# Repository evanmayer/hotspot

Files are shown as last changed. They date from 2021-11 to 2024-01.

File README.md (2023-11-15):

This repo contains code that is a part of the [TIME collaboration](https://ui.adsabs.harvard.edu/abs/2014SPIE.9153E..1WC/abstract).

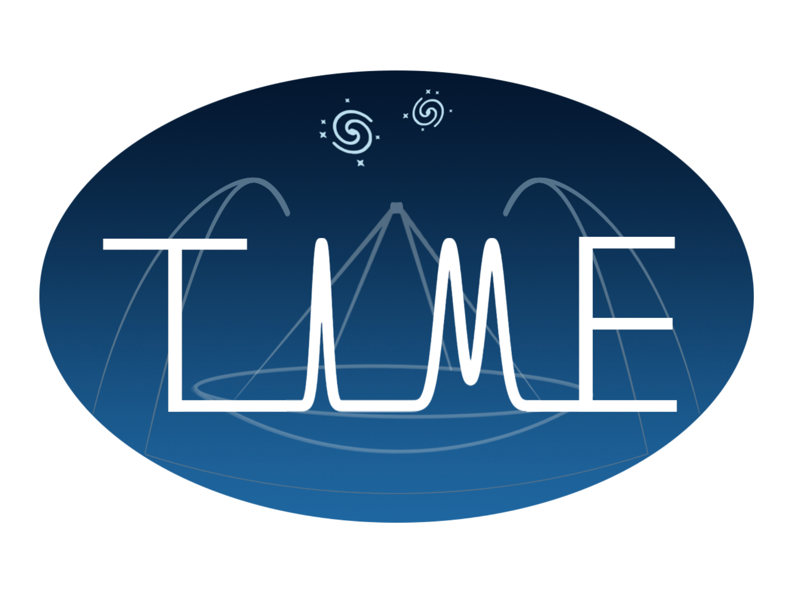
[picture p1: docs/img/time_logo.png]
TIME Collaboration


Logo by Guochao (Jason) Sun.

# hotspot

Code for driving a cable-driven parallel robot for mapping beams on surfaces.

The robot moves and controls switchable thermal infrared sources to scan a 2D x-y plane, and is capable of absolute accuracy at the <3 mm level over a workspace ~0.40m x 0.40m.

## Running

Run `python main.py -h` for the docstring describing the command line interface.

### Example

```bash
python main.py ./data/input/geometry/frame.csv ./data/input/profiles/circle.csv
```

## Other Documentation

See the [HOWTO](HOWTO.md).

## Contributing

### Testing
Testing is accomplished with `pytest`. Passing tests are a prerequisite for committing code, and new code should come with new tests.

To run the test suite defined in the `tests` dir, change dir to the toplevel dir of the repo and execute 
```bash
pytest
```

### Pushing changes
If you need push permissions, message me. Otherwise, you may fork, create a new branch with your changes, and fill out a Pull Request to have the changes reviewed and merged in.

### How did you make your algorithm flowcharts?
[diagrams.net](https://diagrams.net)

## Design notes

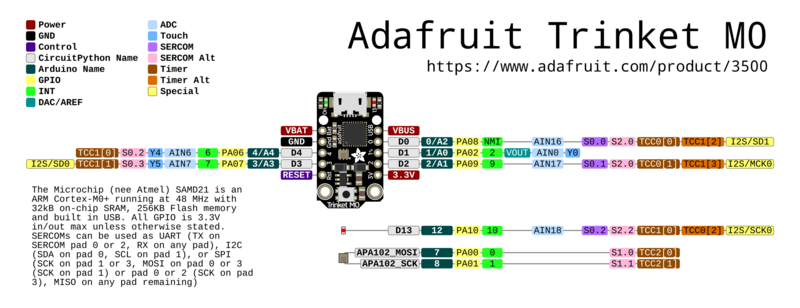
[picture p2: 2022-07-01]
docs/html/docs/img/adafruit_products_Adafruit_Trinket_M0_pinout.png

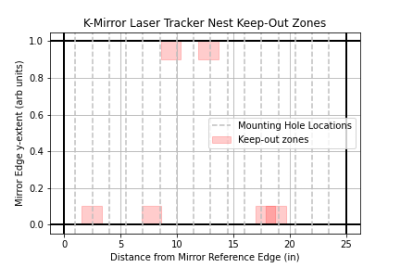
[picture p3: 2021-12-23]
docs/html/docs/img/keepout.png

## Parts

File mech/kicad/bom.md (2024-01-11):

# Bill of Materials

2024-01-11 Evan C. Mayer

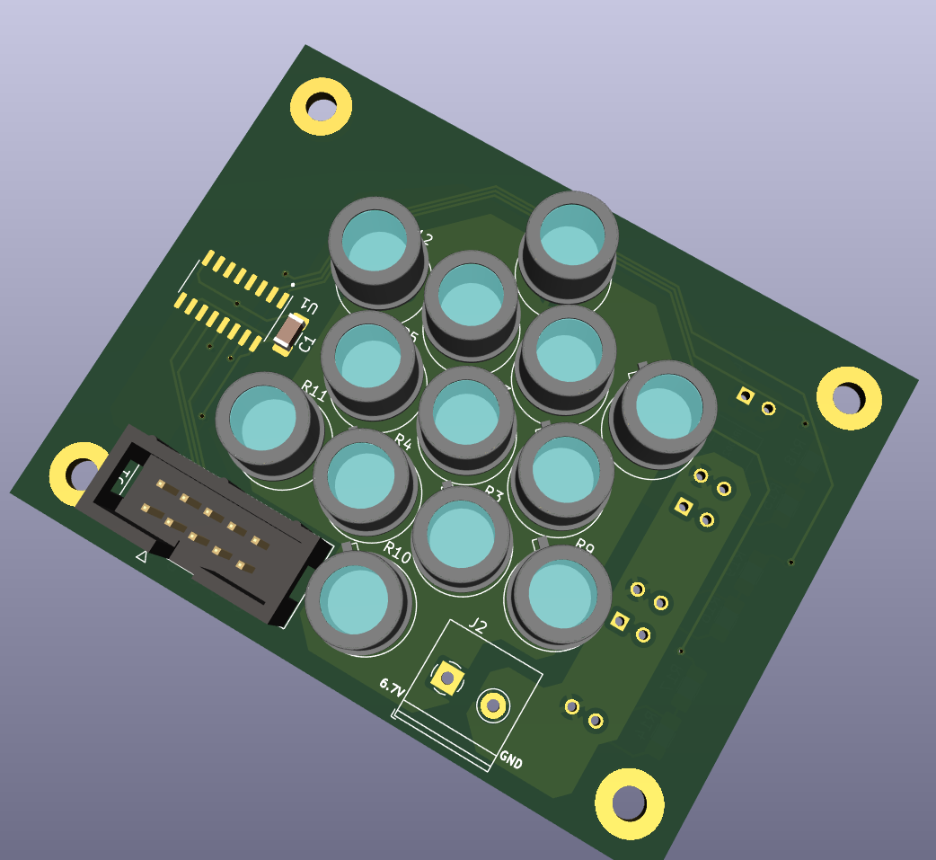
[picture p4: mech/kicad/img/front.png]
Front


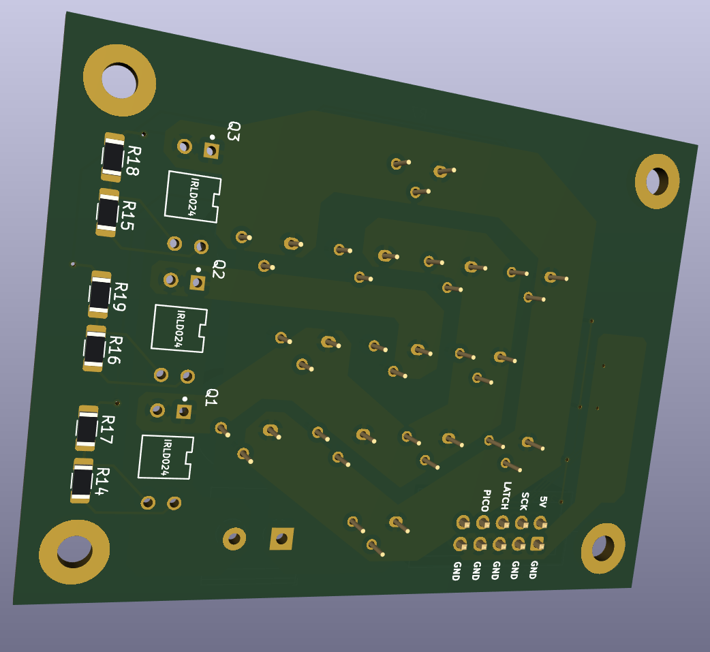
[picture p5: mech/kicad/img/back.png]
Back


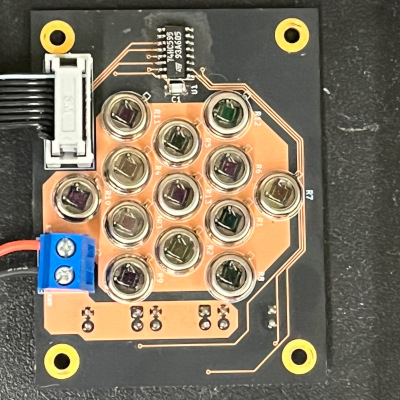
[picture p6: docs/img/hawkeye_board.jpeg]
Built


## Components

Originally developed to be driven by a microcontroller, with each ring selectable via a shift register circuit. If you send a logic-level square wave to MOSFETs some other way, you may omit the items necessary for the shift register driver circuit, marked with an asterisk.

| Part Name | Vendor | Part No. | Link | Qty. | Approx. Cost (USD ea.) | Rationale |
| -- | -- | -- | -- | -- | -- | -- |
Modulated Infrared Source | Hawkeye Technologies | IR-50 | [Link](http://www.hawkeyetechnologies.com/source-selection/pulsable/#ir5x/) [Alt.](https://shop.boselec.com/products/ir-50-ir-55) | 13 | 70.00 | Infrared Emitter |
| Carrier Board | Oshpark | - | [Link](https://oshpark.com/shared_projects/rne2hvI5) | 3 | 10.03 | Assembly/Signal/Power delivery |
| Power MOSFET | Digikey | IRLD024 (sub. IRLD024PBF) | [Original](https://www.digikey.com/en/products/detail/vishay-siliconix/IRLD024/51139) [Sub.](https://www.digikey.com/en/products/detail/vishay-siliconix/IRLD024PBF/812492) | 3 | 1.88 | Power switching via logic-level inputs |
| Resistor 1 | Digikey | RMCF1206JT100R | [Link](https://www.digikey.com/en/products/detail/stackpole-electronics-inc/RMCF1206JT100R/1757426) | 3 | 0.10 | Voltage divider upper. Any 100 Ohm 1/4 W SMD 1206 package. |
| Resistor 2 | Digikey | RMCF1206FT10K0CT-ND | [Link](https://www.digikey.com/en/products/detail/stackpole-electronics-inc/RMCF1206FT10K0/1759669) | 3 | 0.10 | Voltage divider lower. Any 10 kOhm 1/4 W SMD 1206 package. |
| Terminal block | Tri-tek | PHITB132 (sub. TO0201520000G-ND) | [Original](https://www.tritekelectronics.com/wire-termination/terminal-blocks-and-barrier-strips/philmore-tb132) [Sub.](https://www.digikey.com/en/products/detail/amphenol-anytek/TO0201520000G/4953320) | 1 | 0.50 | Power wire connection |
| Shift Register* | Digikey | NTE74HC595T | [Link](https://www.digikey.com/en/products/detail/nte-electronics-inc/NTE74HC595T/11650421?s=N4IgTCBcDaIHYBcCmB2ALACQMIFYCcOIAugL5A) | 1 | 0.55 | Addressable outputs for power switching |
| I2C capacitor* | Digikey | 2368-SMC1206Z104-ND | [Link](https://www.digikey.com/en/products/detail/nte-electronics-inc/SMC1206Z104/11644126) | 1 | 0.05 | I2C noise decoupling capacitor |
| Ribbon cable termination* | Digikey | MSC10A-ND | [Link](https://www.digikey.com/en/products/detail/3m/89110-0001/229679) | 1 | 1.45 | Mates to pins on board header |
| I2C header* | Digikey | 30310-6002HB-ND | [Link](https://www.digikey.com/en/products/detail/3m/30310-6002HB/1237393) | 1 | 0.75 | Provides pwr, I2C header to shift register on board |
| I2C cable* | Adafruit | 3890 | [Link](https://www.adafruit.com/product/3890) | 1 | 3.95 | Sub. any 5-10 conductor 28 AWG ribbon cable if flexible silicone insulation not needed.
| Adafruit Trinket M0 Microcontroller* | Adafruit | 3500 | [Link](https://www.adafruit.com/product/3500) | 1 | 8.95 | Sends bytes to shift register over I2C to chop IR source banks on/off. Sub. any Arduino-compatible microcontroller, with slight code changes.

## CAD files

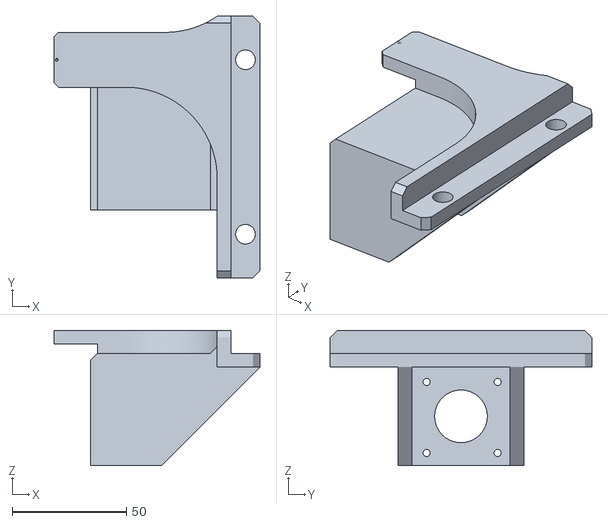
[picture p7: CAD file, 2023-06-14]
mech/3d_prints/motor_mount_thin_mirror.stl
90.0 x 114.3 x 59.0

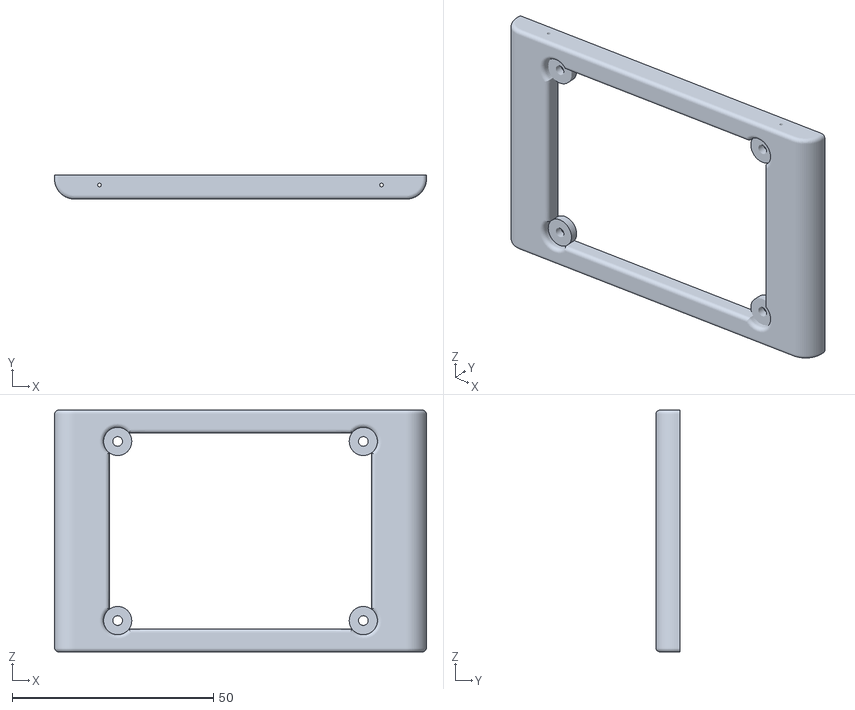
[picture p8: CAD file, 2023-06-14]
mech/3d_prints/hawkeye_raft.stl
92.3 x 6.00 x 60.0

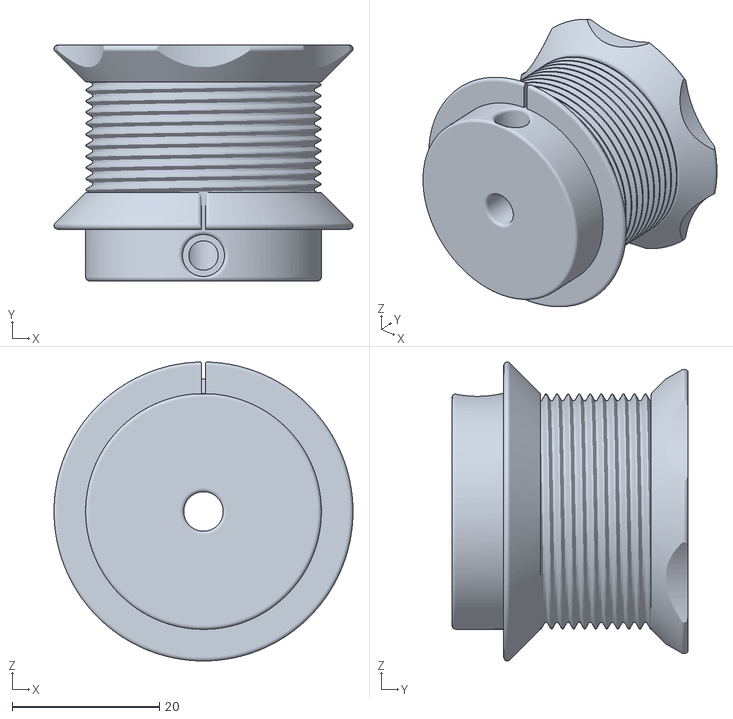
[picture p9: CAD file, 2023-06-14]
mech/3d_prints/drum.stl
40.6 x 32.0 x 40.6

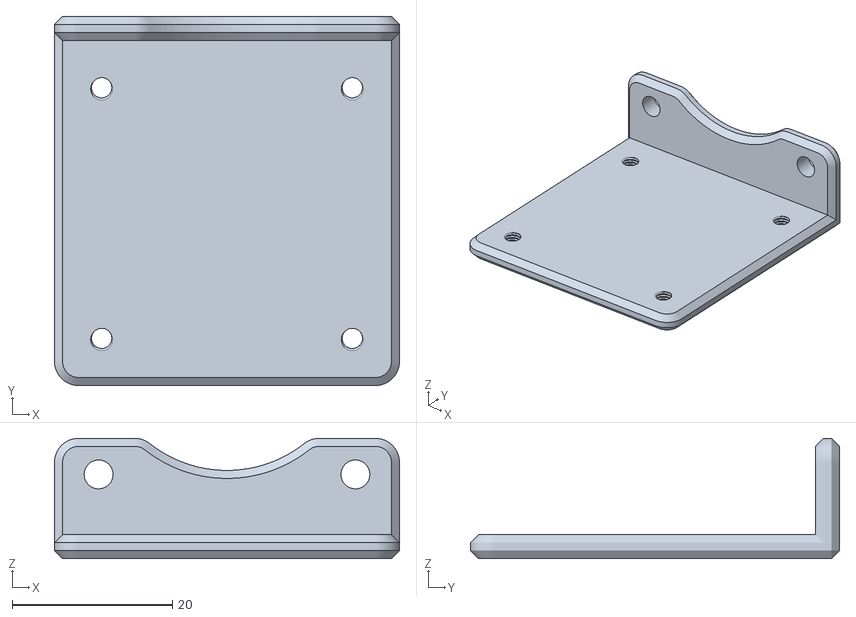
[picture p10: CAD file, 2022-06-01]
mech/3d_prints/ezstepper_bracket.stl
43.0 x 46.0 x 15.0

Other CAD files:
mech/3d_prints/motor_mount_thin.stl

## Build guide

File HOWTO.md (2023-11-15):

# How To

This doc contains instructions for various tasks related to setting up and running the `hotspot` mirror mapper.

#### What is `hotspot`?

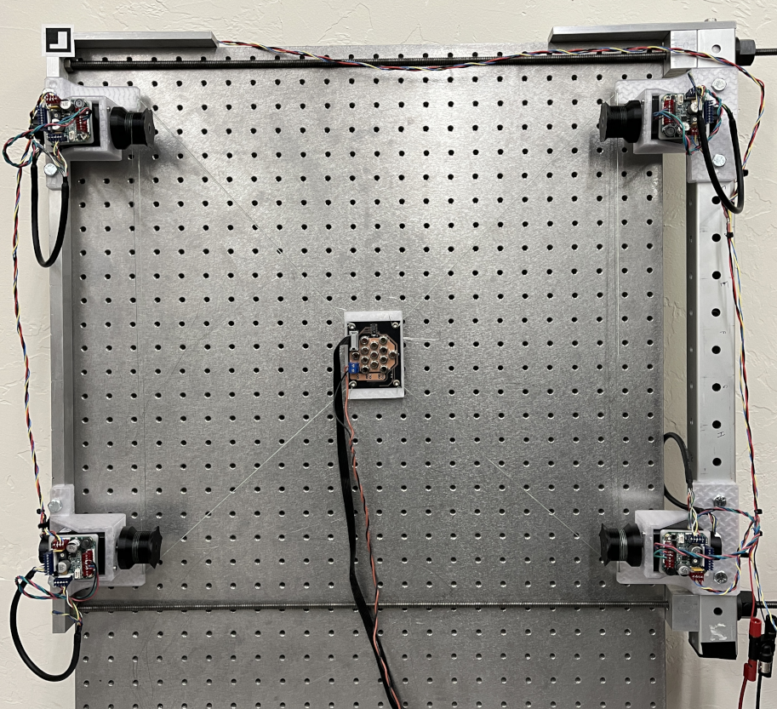
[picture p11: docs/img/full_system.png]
entire system


`hotspot` is a planar cable-driven parallel robot (CDPR), with four stepper motors that move a central raft of hot IR sources by changing the length of cables attached to it. The cables are fixed to an adjustable frame. The frame can clamp to any rectangular surface, but it was designed to clamp to various relay mirrors that couple radiation from the sky to the TIME spectrometer inside the receiver cabin on the ARO 12 meter telescope on Kitt Peak, allowing an electronically controlled, hot, IR-emitting source to be swept across the mirror to observe the detectors' spatial response.

#### What is this document?

This document is a comprehensive how-to on setting up, maintaining, and running the mirror mapper. It contains all the information that would be needed to replace and reconfigure major components of the system, however unlikely that may be.

It is organized in order of information flow: from the operator (you!) logging into the control computer, to setting up the software environment, connecting the power and signal cables, assembling the mapper frame, creating input files, mounting it on various mirrors, and operating the mapper. 

## Using the control computer

The mapper motors are controlled by running the `main.py` application on a computer with a [USB-to-RS485 adapter](https://www.uotek.com/pro_view-122.html). The IR sources are controlled via a USB cable connected to a microcontroller. You should check out the `hotspot` repo if you wish to run the mapper or [generate new input files](#ok-but-is-there-an-easy-way-to-make-a-new-one).

## Setting Up the Environment

To run `hotspot`, you must satisfy the dependencies. They are enumerated in `environment.yml`, a human-readable file that can be ingested by the `conda` Python package manager.

#### Is the environment set up?

First, check that the environment setup has not been done before. If 

```bash
conda activate hotspot
```
succeeds, skip to [software testing with pytest](#software-testing-with-pytest).

### Anaconda

#### Is Anaconda set up?

If the Python environment/package manager [Anaconda](https://www.anaconda.com/) does not exist on the computer you're running this on, I recommend installing Miniconda according to [the instructions](https://docs.conda.io/en/latest/miniconda.html#installing).

Once that is done, we are ready to set up the `hotspot` environment. `conda` environments keep a project's dependencies from polluting your computer's environment and make sure they all play nicely together. `conda` allows specifying the dependencies needed in a file with a `.yml` extension. This is done for you. Create the `hotspot` conda env with

```bash
conda env create -f environment.yml
```

It should install things like `numpy` and `matplotlib`, as well as libraries for the hardware, such as the `pyserial` library for driving the steppers. There are also packages for documentation.

> **NOTE:** packages needed for post-processing of photos to measure mapper performance or for producing predicted beam maps using the code in the `verification/` folder are not covered by this `.yml`. Aside from OpenCV they are just standard scientific Python packages, so the requirements should be easy to meet if this code is needed.

### Keeping things up to date

If you need to install something new later on with `conda install` or `pip`, remember to update `environment.yml` by doing 

```bash
conda env export --from-history | tee environment.yml
```

If your `environment.yml` has been updated, and you need to update your env with the new `environment.yml`, do

```bash
conda env update --file environment.yml --prune
```

## Software Testing with `pytest`

In order to verify that basic low-level functionality is unbroken, run `pytest` from the toplevel directory of the repo.

## Power

### Motors

#### Do the motor driver boards have power?

Each motor is controlled by an [AllMotion EZStepper EZHR17EN](https://www.americancontrolelectronics.com/ezhr17en). These are [chopper driver](https://homepage.divms.uiowa.edu/~jones/step/current.html#pwm) boards that accept 10-40 V input.

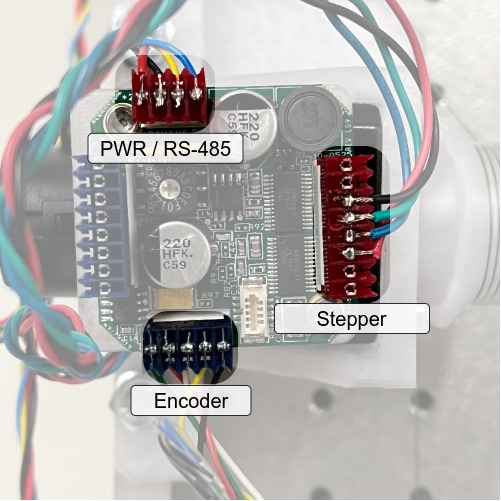
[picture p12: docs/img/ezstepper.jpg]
photo of EZStepper board


Configure a constant-voltage DC power supply to provide:

* 24 V
* 4 A

The EZStepper drivers are configured in software to draw 50% of the rated 2 A current = 1 A each, for a total of 4 A. In use, the motors may draw somewhat less current.

> **Note:** See the AllMotion/American Control Electronics wiring diagram to identify the Vin and GND inputs.

### Hawkeyes

#### Do the Hawkeyes have power?

The Hawkeyes are mounted on a PCB and powered by a power supply connected to the screw terminal. Positive and ground terminals are labeled on the PCB silkscreen (white text).

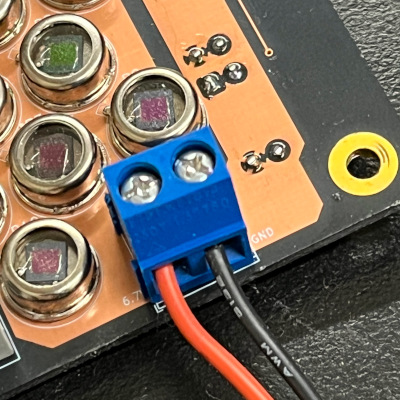
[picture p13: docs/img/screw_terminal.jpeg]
photo of screw terminal


Requirements:

* 6.7 V (constant voltage)
* ≥ 2 A

The Hawkeye IR-50 source temperature depends on the voltage applied, and the current draw depends on the voltage (see datasheet in `pdf` dir). The design target temperature is 750 C, requiring a voltage of 6.7V and a current of ~134mA per source, for a total current draw of ~1.74A when all sources are turned on. In practice, Hawkeye sources have not drawn quite this much current.

There will be some voltage drop at the screw terminal; this is normal. If one source is powered, the voltage drop is negligible, but if all 13 sources are powered, the voltage drop is approximately .22 V. Do not attempt to compensate for this at the power supply! If you turn up the supply voltage to 6.9 V to get 6.7 V under a 13 source load, a load of a single source will see 6.9 V, drastically reducing its lifetime.

### Hawkeye Microcontroller

The Hawkeye sources are turned on and off by an Adafruit Trinket M0 microcontroller. It gets 5V power via a micro USB cable.

#### Does the microcontroller have power?

The Trinket M0's power LED will illuminate when it is connected to the USB port. The Trinket GND pin should be connected to the Hawkeye power supply's ground terminal.

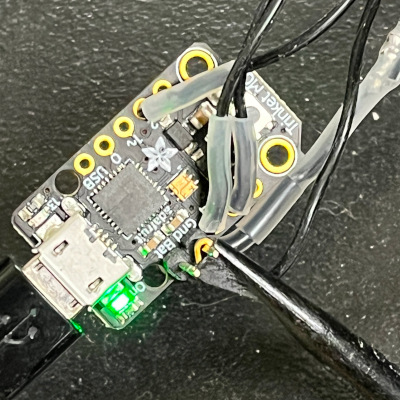
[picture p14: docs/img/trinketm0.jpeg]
photo of mcu on


## Frame

#### Is the frame fully assembled?

The 3D printed stepper motor mounts are attached to the beam mapper frame by 5/16-18 x 2" or 2.25" bolts with nyloc "jam" nuts.

Two aluminum registration tabs are screwed into the end of each frame piece opposite the black plastic end caps, using a 5/16-18 x 1/4" screw. They are long enough to reach an edge of the mirror regardless of if the mirror's corners have been machined off. 

> **NOTE:** These tabs register the frame to a third edge of the mirror, so **it is important that they not be bent**.

Long 5/16-18 steel threaded rods connect the two halves of the frame. On one end of the threaded rods, threads in the aluminum extrusion provide clamping force. On the other end of the threaded rod, a slide-adjust nut with a thumb button allows easily changing the distance between clamping surfaces, and applies clamping force to the outside of the opposite aluminum extrusion. Care should be exercised with this slide-adjust nut, as pressing the button will release any tension on the threaded rod.

## Serial Communications

We will be talking to devices over serial. 

### Windows

Windows users may need to open `hotspot/constants.py` and edit the `COM` values to match the COM ports assigned to the Hawkeye microcontroller and USB-to-RS485 converter by the OS.

### Ubuntu

On Ubuntu, our user must be a part of a special group to talk to devices over serial. To see the groups your user is a part of, type `groups` in a command prompt.

Add yourself to the `tty` and `dialout` groups, then log out and back in to have the changes take effect:

`sudo usermod -a -G tty $USER`

`sudo usermod -a -G dialout $USER`

## Motion Outputs

### Motors

#### Can the computer talk to the motor drivers?

The EZHR17EN stepper drivers receive commands from a control computer running the `hotspot` software as bytes over the [RS485](https://hackaday.com/2022/04/05/hacker-dictionary-rs-485-will-go-the-distance/#more-528633) physical layer.

> **Note:** Refer to the AllMotion/American Control Electronics EZHR17EN wiring diagram to verify that the RS485 communications connection is correct.

The control computer needs either a 9-pin serial output port, or a USB-to-RS485 adapter to send bytes out over the RS485 bus. The inverting/non-inverting outputs are blue and yellow wires. If you are connecting your adapter to the bus for the first time, you may have to [guess incorrectly](https://en.wikipedia.org/wiki/RS-485#Signals) and swap the wires before it will work.

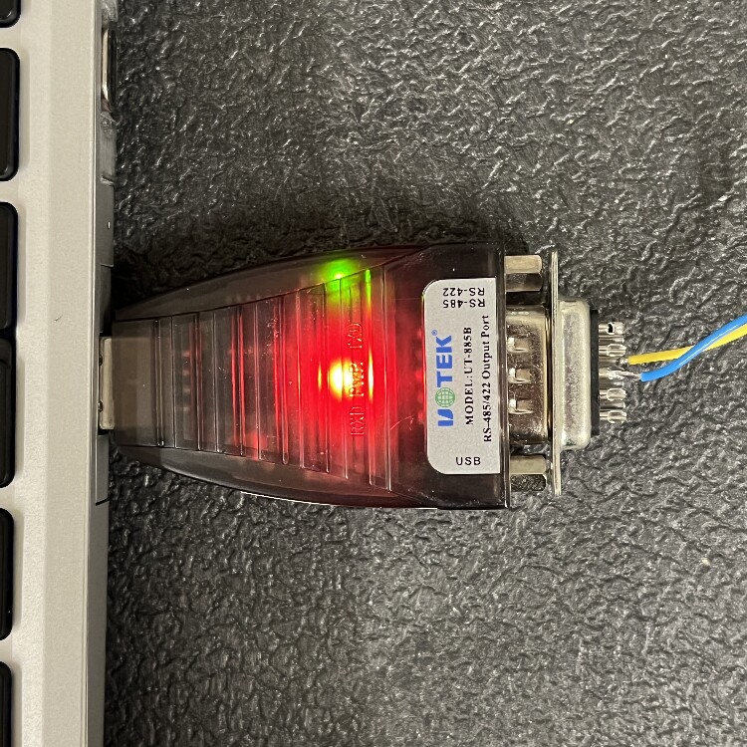
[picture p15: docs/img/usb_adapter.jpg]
photo of USB-RS485 adapter


The motor drivers must have power and ground (via the 24 VDC power supply) to receive commands.

> **NOTE:** RS-485 Connections ought to have a ground wire, although you don't see one pictured here. This is to ensure the differential signal at each receiver is biased correctly. If you experience communication issues on the RS-485 bus, ensure proper grounding.

#### Can the motor drivers command the motors?

> **Note:** Refer to the AllMotion/American Control Electronics EZHR17EN wiring diagram to verify that the motor winding connections are correct.

The stepper motors themselves have NEMA-17 spec hole patterns, which mate to the 3D printed motor mount brackets which are attached to the beam mapper frame. Each stepper motor should be attached to its motor mount using M3 x 0.5 x 10 mm screws. If attaching motors for the first time, use lubricant, because metal on plastic will be squeaky.

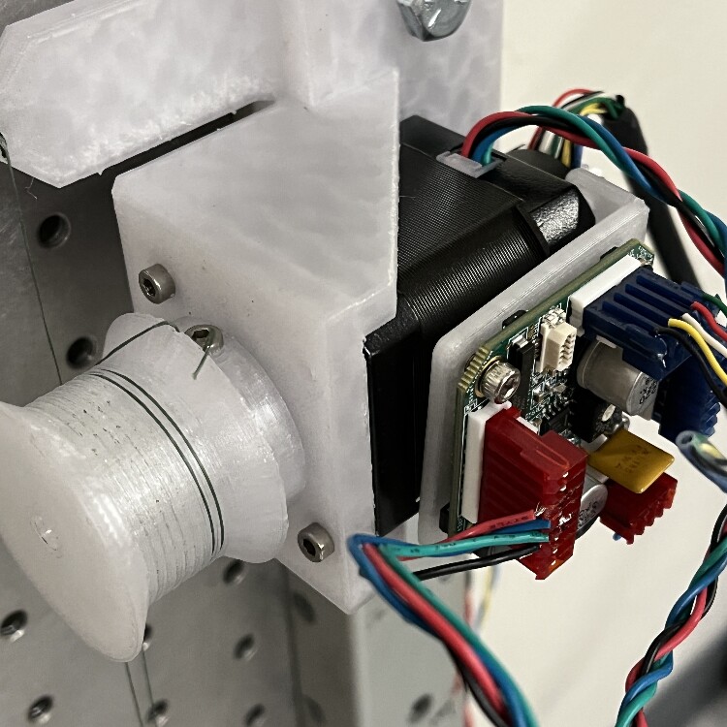
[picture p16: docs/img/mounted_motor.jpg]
photo of stepper mounted on motor mount


At this point, it is important to consider the mapping of motor driver board address -> stepper motor -> motor mount -> corner of beam mapper frame -> corner of raft. The `Executive.__init__()` function in `executive.py` specifies this mapping, so the motor installation location and stepper instance in `__init__()` should match, to ensure the correct motor commands are sent to the correct stepper. The stepper driver boards are addressable with a selector switch on top. Match the address selector to the correct corner of the raft in the `__init__()` function.

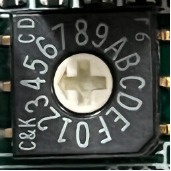
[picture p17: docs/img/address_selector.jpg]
photo of address selector switch


#### Can the encoders provide position feedback?

The EZHR17EN boards are capable of reading out [quadrature encoders](https://cdn.sparkfun.com/datasheets/Robotics/How%20to%20use%20a%20quadrature%20encoder.pdf) affixed to the stepper shafts. Encoder feedback is critical for accurate positioning of the raft.

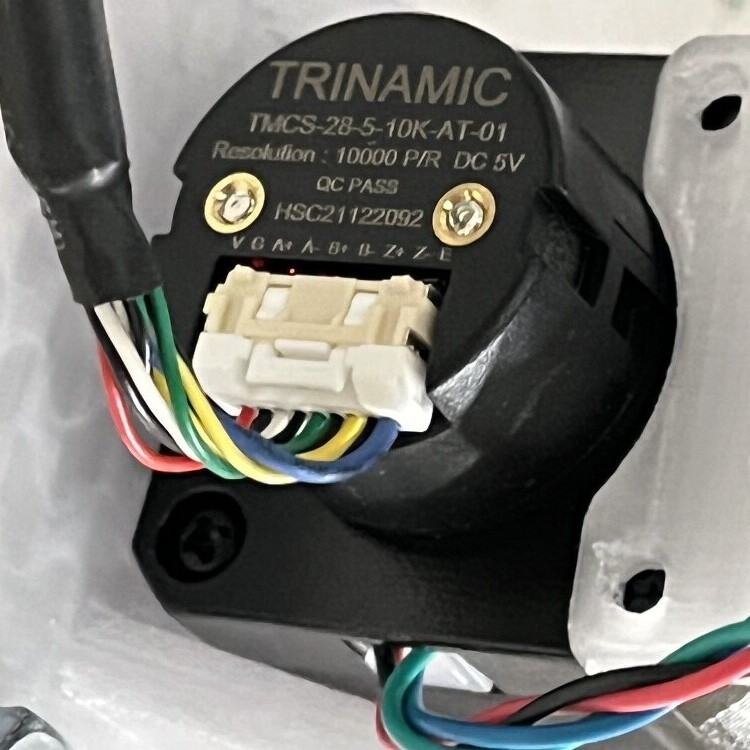
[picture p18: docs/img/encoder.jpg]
photo of stepper encoder


> **Note:** Refer to the AllMotion/American Control Electronics EZHR17EN wiring diagram to verify that the encoder connections are correct.

### Spools

#### Can the motors make the lines longer and shorter?

The stepper motors drive winch-like drums directly, to change the length of the cables predictably. They are cylindrical drums with helical threads to accept the cables.

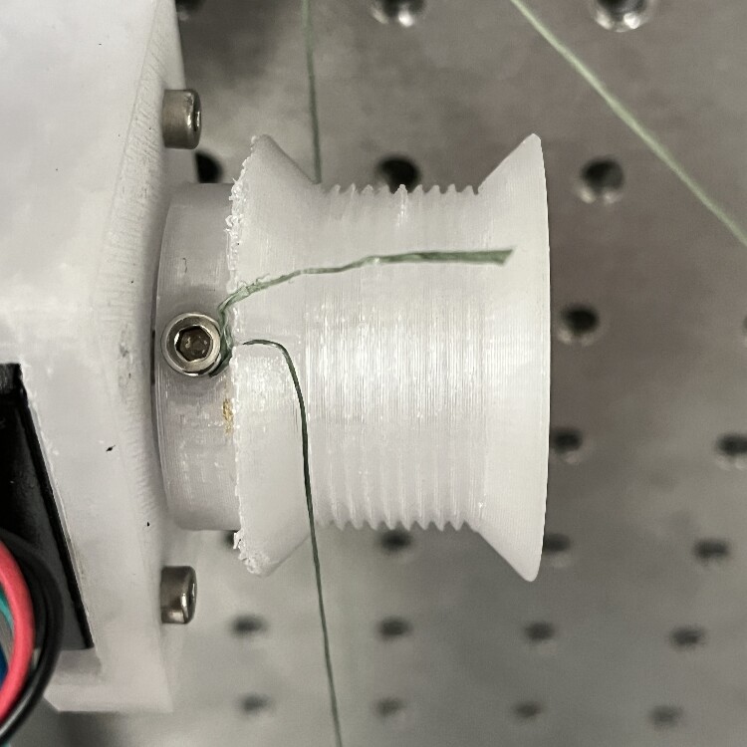
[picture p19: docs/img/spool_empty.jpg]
photo of drum with cable extended, at longer rotational limit


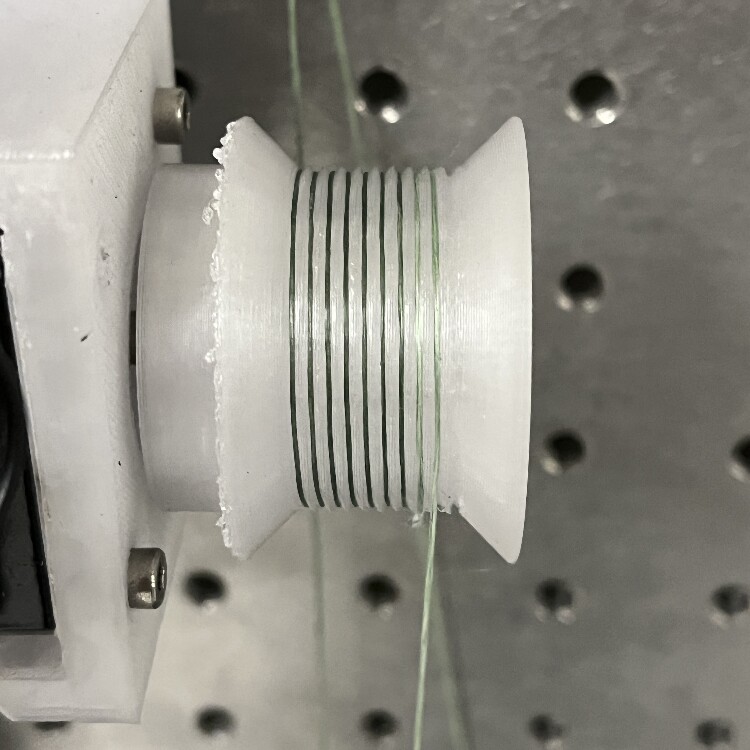
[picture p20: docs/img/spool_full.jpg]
photo of drum with cable extended, at shorter rotational limit


If they are not already attached, the cable drums should be fixed to the 5 mm stepper motor shaft via one M3 setscrew.

The screws mate to steel threaded inserts that are pressed into the PETG plastic spools.

The fishing line is affixed to the each spool by wrapping it around the setscrew and screwing it in to the threaded recess on the spool circumference.

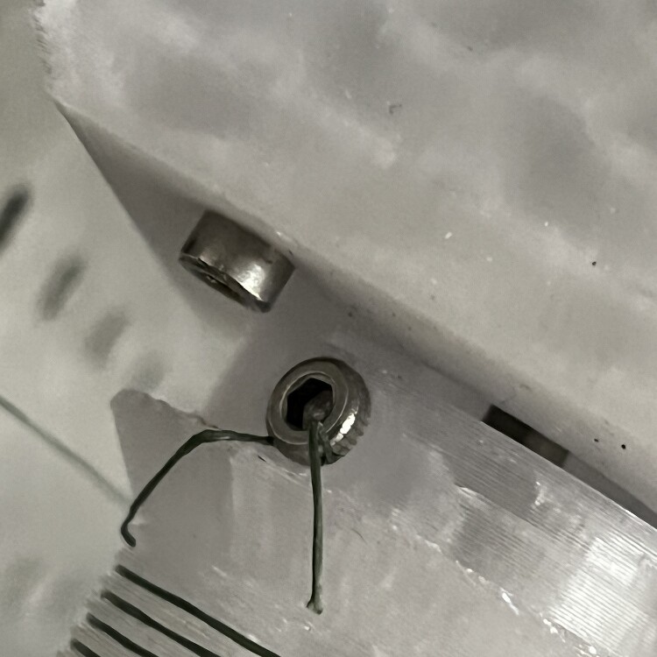
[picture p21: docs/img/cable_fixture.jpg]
photo of cable in screw


> **NOTE:** Positive motor rotation is defined by convention to spin the shaft clockwise when viewed from the rear of the motor. Cables should be oriented relative to the spool such that a positive motor rotation produces a positive cable length change (i.e., cable is played out from the spool), and a negative motor rotation winds cable onto the spool.

Since helical threads change the position along the drum $y$ that the cable exits as a function of motor position, the actual length of cable change for a given rotation depends on the thread pitch. Also, a controlled spooling mechanism is usually required. In this case, the corresponding eyelet is located some distance from the spool to achieve controlled spooling with less complexity.

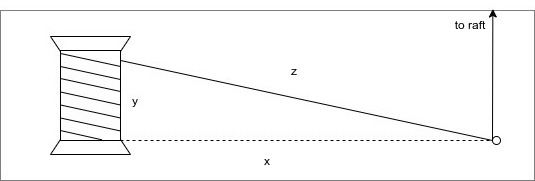
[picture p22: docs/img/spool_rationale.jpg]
Drum rationale


After attaching the cables to the spools, the other end should be threaded through the ~.9mm hole in the motor mount bracket on the opposite E-W side of the frame.

> **NOTE:** All cables should be cut long enough to permit the raft to visit each corner of the frame, even when the frame is as far apart as it can be (~25.5").

Finally, excess cable should be wound onto the drum by hand, under tension, to ensure the cable is seated in the drum's grooves.

## Radiation Outputs

#### Will moving the cables move the Hawkeyes?

The end effector of this robot is a rectangular raft carrying several Hawkeye Technologies [IR-50](http://www.hawkeyetechnologies.com/source-selection/pulsable/) emitters. The robot drives the centroid of the effector to a specified position, and the control algorithm performs a sequence of flashes using a number of the emitters to enhance the detectability of the signal in the IR receiver output data.

photo of raft

Pass the cables that emerge from the corner eyelets to the closest eyelets on the raft. Wrap the ends of the fishing line around the screws in each corner of the raft, and screw them down.

#### Can the computer command the Hawkeyes?

The Hawkeye IR sources are arranged in roughly 3 concentric circles. Each circle is a separately controllable group of sources, which can be turned on and off by the control software. The first group is a single center source. The second group is the inner ring of six sources surrounding the center. The third group is the outer ring of six sources. Turning on more sources increases the intensity that the TIME receiver sees; this may be necessary for mapping optics where the beam is less concentrated.

Each group is turned on and off by a MOSFET on the raft. The MOSFET gates are controlled by the outputs of a [shift register](https://en.wikipedia.org/wiki/Shift_register) chip. The shift register multiplexes 8 bits (a byte) received at its input to its 8 output pins. Only 3 of the 8 are connected to MOSFETs.

The shift register receives a byte from an Adafruit Trinket M0 microcontroller over [SPI](https://en.wikipedia.org/wiki/Serial_Peripheral_Interface) via the black silicone ribbon cable, which should be hooked up to the grey connector on the raft. The connector pinout is on the back of the PCB. The other end of the cable is soldered to the Trinket M0 pins.

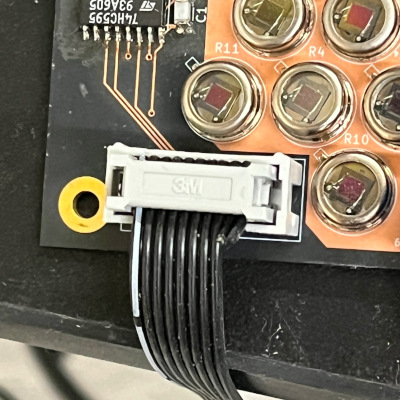
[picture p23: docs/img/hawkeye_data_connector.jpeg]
photo of Hawkeye data connector


The data connection pinout from the Trinket M0 to the ribbon cable connector is as follows:

* Trinket M0 GND → GND
    * The shift register GND must be the same as the microcontroller ground. This should be grounded to the Hawkeye power ground as well.
* Trinket M0 BAT → 5 V
    * 5 V from the USB connector appears here. This powers the shift register.
* Trinket M0 2 → LATCH
    * This pin goes low when an SPI transfer is started
* Trinket M0 4 → CLK
    * This pin pulses during an SPI transfer to delineate bits to the shift register.
* Trinket M0 5 → PICO (peripheral input, controller output)
    * This pin goes low or high during an SPI transfer to send bits to the shift register.

photo of mcu on

The Trinket M0 receives a byte from the control computer over a USB serial connection and forwards it to the shift register over SPI.

| Profile Input File .csv: `flasher_cmds` value | Trinket M0 SPI Output | Bit Representation (Shift Register Outputs) | Trinket M0 RGB LED Color | Hawkeyes On          |
|-----------------------------------------------|-----------------------|---------------------------------------------|--------------------------|----------------------|
| 0                                             | 0                     | 0000000                                     | (Dimmed)                 | None                 |
| 1                                             | 1                     | 0000001                                     | Red                      | Center               |
| 2                                             | 2                     | 0000010                                     | Green                    | Inner                |
| 3                                             | 3                     | 0000011                                     | Yellow                   | Center, Inner        |
| 4                                             | 4                     | 0000100                                     | Blue                     | Outer                |
| 5                                             | 5                     | 0000101                                     | Purple                   | Center, Outer        |
| 6                                             | 6                     | 0000110                                     | Cyan                     | Inner, Outer         |
| 7                                             | 7                     | 0000111                                     | White                    | Center, Inner, Outer |

The control computer will flash whichever group of Hawkeyes is specified by the input profile .csv file at 5 Hz.

### Cable Maintenance

#### What if a cable breaks?

The original cable is Spiderwire EZ Braid braided dyneema fishing line (50 lb pull strength), chosen for its stretch resistance. A replacement can be found at any tackle store or Wal-Mart, but a spool of extra cable should already be stored with the beam mapper.

Cable length should be carefully sized to allow the raft to reach all corners of the workspace, but with as little extra length as possible at the maximum allowed separation of 25.5".

## Coordinate System

 In order for the raft to be moved to a meaningful position in mirror-space, coordinates must be referenced to sensible locations where the mirror edges and robot frame register to one another.

 * **x-axis**: plane of contact between the "south" frame and an edge of the mirror
 * **y-axis**: plane of contact between the "west" side aluminum registration tab and a perpendicular mirror edge.
 
 The coordinate system of the robot therefore has its origin at the SW corner, where the aluminum alignment tab on the fixed frame meets the aluminum extrusion face.
 
## Input Files

There are two types of input files: `geometry` and `profile`.
Read on to learn what they are for and what is inside each.

#### Ok, but is there an easy way to make a new one?

`.ipynb` files are provided in the `data/input/*` directories to assist with making these input files. Most likely, you will only need `data/input/create_profile.ipynb`.

You will need Jupyter installed on the computer running this notebook. Then simply copy the new files to the `/data/input/*` directory.

### Geometry
Geometry files are one-line .csv files in `data/input/geometry`. 

`create_geometry.ipynb` is provided to script the creation of geometry files.

Each one defines the physical setup of the robot when it is in a certain configuration, for instance, when it is installed on a mirror of a certain dimension. Each column entry describes an aspect of the physical setup of the system. A simplistic example:

| sw_0  | sw_1  | nw_0  | nw_1  | se_0  | se_1  | ne_0  | ne_1  | w  | h |
|:--:|:--:|:--:|:--:|:--:|:--:|:--:|:--:|:--:|:--:|
| 0  | 0  | 0  | 1  | 1  | 0  | 1  | 1  | .1  | .1 |

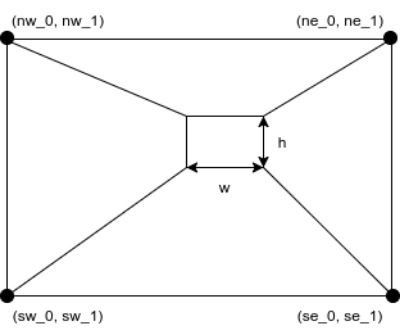
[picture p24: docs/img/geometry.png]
geometry


Each corner point is the location of an **eyelet** through which the cable passes, expressed relative to the SW origin, described above. The width and height of the raft are defined by the separations between eyelets on the raft through which the cable passes.

> **NOTE:** If the dimensions of the frame eyelets have been measured relative to each edge, the y-positions of the corner eyelets can be calculated as a function of the separation between the aluminum extrusions that make up the support structure and clamping surfaces.

> The eyelets of the motor mounts measured 6.19 +/- 0.5 mm from the frame to the face of the motor mount bracket on the interior of the mapping region, and 7.96 +/- 0.02 mm from the face of the motor mount to the eyelet, for a total eyelet offset from the contact patch of 0.014 +/- 0.001 m. This value will be used to calculate eyelet y-positions as a function of frame separation.

> The eyelet positions should not ever change in the x-direction, unless the motor mounts are removed from the aluminum frames.

### Profile

Profile files are multi-line .csv files in `data/input/profiles`. Each line defines a new position to which the robot should move, in the coordinate system defined above, and which group of Hawkeye sources should be flashed.

`profiles/create_profile.ipynb` is provided to script the creation of profiles.

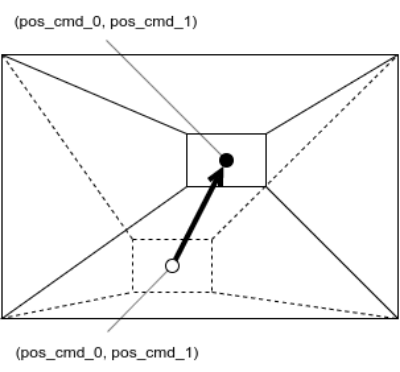
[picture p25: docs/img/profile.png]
profile


Upon reaching each location in the profile, the robot is programmed to flash Hawkeye sources on and off (default: 10 "on" states, 50% duty cycle, 5 Hz). Which group of sources is enabled is configurable with the `flasher_cmds` column in the profile .csv. See the table in the previous section. Some examples follow.

For example, to move to a single coordinate and flash all three groups of Hawkeyes:

| flasher_cmds | pos_cmd_0s | pos_cmd_1s |
|:------------:|:----------:|:----------:|
| 7            | .5         | .5         |

to move to a single coordinate and flash only the center Hawkeye:

| flasher_cmds | pos_cmd_0s | pos_cmd_1s |
|:------------:|:----------:|:----------:|
| 1            | .5         | .5         |

to move to a single coordinate and flash the center and inner ring Hawkeyes:

| flasher_cmds | pos_cmd_0s | pos_cmd_1s |
|:------------:|:----------:|:----------:|
| 2            | .5         | .5         |

Building up a sequence of these moves allows a shape to be scanned.

## Output Files

Output files store telemetry for each run in `data/output`. They are timestamped `.hdf5` files.

## Physical Installation

### General tips

* Having two people helps.

* _<span style="color:red">**SAFETY ALERT: BE VERY CAREFUL** about touching the buttons on the black slide-adjust nuts</span>_
    * If you are loosening or tightening the mapper down to anything, when the mapper is under tension, touching the button could release tension rapidly, _**potentially causing a fall**_, potentially on to a _**very expensive mm-wave optic,**_ which you do not want.
    * If you are adjusting the mapper spacing and you let them off of the threaded rod, *they will disassemble themselves rapidly*. You don't want to lose any parts.

* Bring a USB extension cable to make moving the frame to various mirrors easier. That will extend RS485 connection, allowing you to stand or sit in a more comfortable spot.

* If you can't have the shutter open to let the optical chain see cold sky, bring a lot of flat Eccosorb panels. Don't bother trying to tape Eccosorb to anything. Tape won't stick. Just pinch it in between the mirror and threaded rod. This also helps keep the threaded rod or raft from marring the mirror surface, which is very important.

* Keep as much stuff (power/data cables, hands, heads, ladders) as possible out of the path of the beam.

### K1

Underneath shutter, highest up. Put a step ladder inside the K-mirror frame to make the lift easier. Route Hawkeye cables around back of K1 and down.

`python main.py ./data/input/geometry/K1.csv ./data/input/profiles/K1_<profile>.csv`

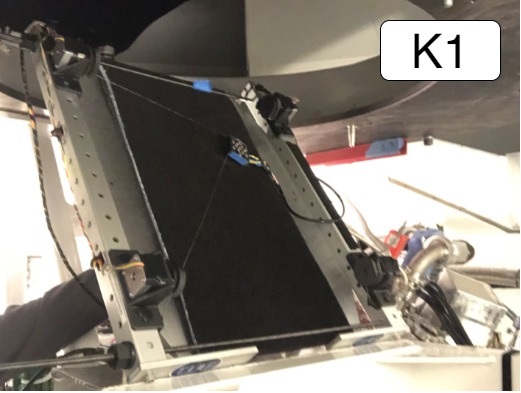
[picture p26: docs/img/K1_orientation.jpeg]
K1


### K2

Should be easy. Remove the anti-head-smasher foam first to get to the bottom clamping surface.

`python main.py ./data/input/geometry/K2.csv ./data/input/profiles/K2_<profile>.csv`

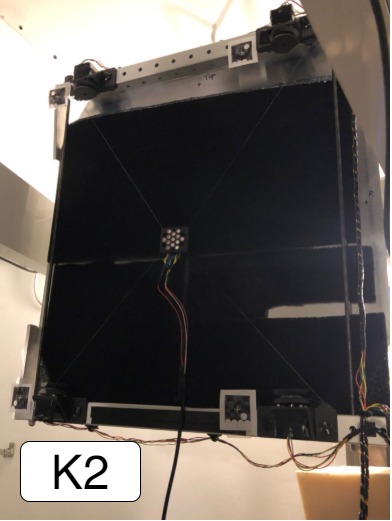
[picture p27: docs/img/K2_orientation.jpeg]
K2


### K3

Pucker factor 11. Have a friend help you mount the mapper; one person to hold the mapper in place, one to secure the slide-adjust nutes. Gravity is working against you, and you're right above F1, but snug things down good and tight when mounting the mapper and you will be fine. I used a crescent wrench on the black slide-adjust nuts for this one, to get a lot of clamping force. _<span style="color:red">**Be careful not to release the slide-adjust nuts when using the wrench.**</span>_

`python main.py ./data/input/geometry/K3.csv ./data/input/profiles/K3_<profile>.csv`

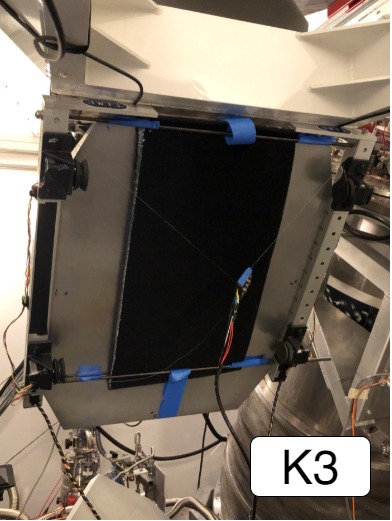
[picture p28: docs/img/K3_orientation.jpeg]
K3


### F1

Another easy one.

`python main.py ./data/input/geometry/F1.csv ./data/input/profiles/F1_<profile>.csv`

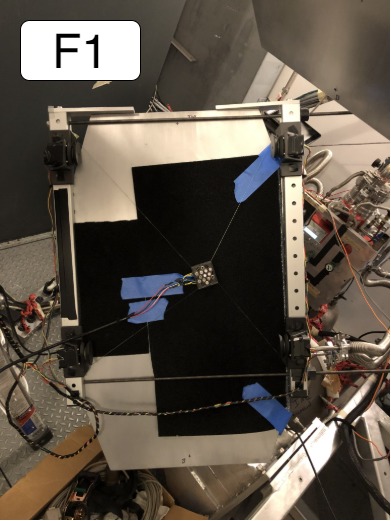
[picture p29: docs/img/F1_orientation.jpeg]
F1


### P2

Easy. It's down on the floor near the wall.

[photo of mapper mounted on P2]

## Operation

When a surface geometry file has been created and the profile for the given shape to be mapped is generated, we are ready to run the program. There should already be geometry and profile files for each mirror in the `data/input` directories.

## Homing

### Pre-mapping checks

1. Make sure that 24 V is being supplied to all driver boards and that the polarity is correct.
2. Make sure that 6.7V is being supplied to the Hawkeyes.
3. Make sure the power supply output is on.
4. Make sure that the cable is wound onto each spool and that no loops of excess cable are trapped underneath the cable wound onto the spools.
5. Check the excess cable played out in the raft's current position. Some excess is fine as long as it doesn't interfere with the raft's motion.
6. Ensure the Hawkeye source power and data cables lines won't interfere with mapper operation, usually, this means routing the cables somewhat along the gravity vector.
7. Ensure the `hotspot` `conda` env is active: `conda activate hotspot`.

### Mapping

1. Start the program with `python main.py ./data/input/geometry/<geometry.csv> ./data/input/profiles/<profile.csv>`
2. Perform a homing calibration: `c`, `RETURN` key. 
3. The motors will drive to each corner in turn, bumping the hard stop three times in order to measure the encoder position where 0 mm of cable is played out. When complete, it will move to the center of the workspace.
4. Verify that the raft reached its home position in the center of the workspace, and that the other axes achieved tension. If not, GOTO 2. If homing succeeded without incident and cables are not taut, check the measurements of the corner eyelets and the raft dimensions provided in the geometry input .csv file.
6. Perform a mapping sequence: `r` (for run), `RETURN` key. 
7. The raft will drive to each location and flash the Hawkeyes at each point in the sequence. Observe the mapper, ensuring the Hawkeye signal cable does not interfere with the mapper.
    1. You may request a mode change at any time. Mode changes are processed at the end of each move.
    2. You may abort the program with `Ctrl+C`.
8. Upon completing a sequence, it may be repeated by requesting the sequence mode again.
9. You may select a different sequence by pressing `s` and following the prompts.

## Reference HTML
The html documentation of the source code and Markdown materials is generated by [portray](https://timothycrosley.github.io/portray/).

To regenerate the documentation, execute:

```bash
portray as_html -m hotspot -o docs/html/ --overwrite
```

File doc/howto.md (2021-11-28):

# How To

This doc contains instructions for various tasks related to setting up and running the beam mapper.

# Setting Up the Environment

First, check that the environment setup has not been done before. If 
```bash
conda activate hotspot
```
succeeds, skip these steps.

## Python Dependencies
### Anaconda
If the Python environment/package manager [Anaconda](https://www.anaconda.com/) does not exist on the Raspberry Pi you're running this on, I recommend installing Miniconda [from here](https://docs.conda.io/en/master/miniconda.html). Get the installer for ARM processors (it has `aarch64` in the name) and follow the online instructions.

Once that is done, we are ready to set up the `hotspot` environment. `conda` allows specifying the packages needed in a file with a `.yml` extension. This is done for you. Create the `hotspot` conda env with

```bash
conda env create -f hotspot.yml
```

It should install things like `numpy` and `matplotlib`, as well as drivers for the hardware, such as Adafruit's `adafruit-circuitpython-motorkit` library for driving the steppers, and the library for controlling the Hawkeye IR sources via the LabJack.

Once that is done, activate the env with 

```bash
conda activate hotspot
```

If you need to install something else, remember to update `hotspot.yml` by doing 

```bash
conda env export --from-history | tee hotspot.yml
```

If your `hotspot.yml` has been updated, and you need to update your env with the new `hotspot.yml`, do

```bash
conda env update --file hotspot.yml --prune
```

# Setting Up the Hardware

## Enable Raspberry Pi Hardware

The raspberry pi should have at least two [motor driver hat boards](https://learn.adafruit.com/adafruit-dc-and-stepper-motor-hat-for-raspberry-pi). These are PCBs with onboard chips that talk to the raspberry pi on an I2C bus via the 2x20 header pins. They issue commands to the motor driver chips, which handle the delivery and timing of greater voltage and current than the raspberry pi is capable of on its own.

Follow the steps for [Enabling I2C communication](https://learn.adafruit.com/adafruit-dc-and-stepper-motor-hat-for-raspberry-pi/installing-software#enable-i2c-1106864-2) from Adafruit. A backup pdf is saved in the `pdf` dir.

## Power

### Motors
The motor driver board must be powered via its own power supply, since the raspberry pi cannot provide the requisite voltage or current. A lab power supply with 12V output is attached to the +/- screw terminal block on the motor driver hat. For stacking multiple hats, jumpers are attached to the screw terminals to route +/- voltage to the additional hats. The motor controllers on each hat are designed to run with 5-12V, with a maximum instantaneous current of ~1.2A.

### LabJack
The LabJack board also needs its own power supply to drive the voltage/current that is switched via the breakout board. A tunable lab power supply is attached to one of the screw terminals labeled "VS#," for "voltage source #," where # is one of the channels, 1-6. The voltage of this power supply will depend on what is hooked up to the switchable terminals. In this case, we are using LEDs to stand in for Hawkeye IR sources, so 3.3V is fine.

## Communication

### Raspberry Pi
You can log in to the raspberry pi via `ssh`. In order for you computer to "see" the raspberry pi, though, they must be on the same network. This can be accomplished a few ways (or order of ease of use):
1. By connecting both computers to a router or network switch that can assigns each connected device an IP address automatically. Wired is easier than [wireless](https://www.raspberrypi.com/documentation/computers/configuration.html#setting-up-a-headless-raspberry-pi).
1. By connecting directly to the pi via an Ethernet patch cable and setting up a [link-local](https://en.wikipedia.org/wiki/Link-local_address) connection
1. By connecting directly to the pi via an Ethernet patch cable and assigning static IP addresses to each host.

The first option is the easiest, but depends on having access to an exisiting network, so limits your connectivity options. If you have access to a Linux machine, the second option is about as easy and more flexible, in my opinion.

 The hostname and password are printed on the bottom of the white plastic case. Once connection is sorted out, ping the pi to make sure:
 
 ```ping timepi.local```
 
 The ssh command goes like this:

 ```ssh -X pi@timepi.local```

 `-X` allows X-forwarding, in case a graphical application (like plotting) is invoked. You will be prompted for a password, which you can find printed on the bottom of the white plastic raspberry pi case.

### Motors

Motors should be connected to the screw terminals of the pi's stepper hat like this:

<img src="img/stepper_wiring.jpg" alt="drawing" width="200"/>

Getting the order right ensures the stepper's coils are energized in the correct sequence to get it to rotate.

The stepper motors have NEMA-17 spec hole patterns, which mate to the 3D printed CFRP motor mount brackets which we will attach to the beam mapper frame. Each stepper should be attached to its motor mount using M3 x 0.5 x 10mm screws. Use lubricant, because metal on CFRP will be squeaky.

At this point, it is important to consider mapping of motor HAT terminal -> stepper motor -> motor mount -> corner of beam mapper frame. The `Executive.__init__()` function specifies this mapping, so the motor installation location and stepper instance in `__init__()` should match, to ensure the correct motor commands are sent to the correct stepper.

In general, the HAT closest to the Pi will be `kit0` (although this can be double-checked by looking at the address - `0x60` is the default I2C address for the hat, which can be changed by bridging the HAT pads A0-A4, so the board addressed by `0x60` will have no pads bridged). The terminal blocks M1-M2 are used for `stepper1` on each HAT, and M3-M4 are used for `stepper2`.

It doesn't matter which terminal maps to which corner, only that the code and physical arrangement agree.

## Spools

The spools are each attached to the 5mm stepper motor shaft via one M3 setscrew. The fishing line is affixed to the each spool by wrapping it around the setscrew and screwing it in to the threaded recess on the spool circumference. 

<img src="img/spool_side_view.jpg" alt="drawing" width="200"/>	

Positive motor rotation is defined by convention to spin the shaft clockwise when viewed from the rear of the motor. Motors should be oriented relative to the cable such that a positive motor rotation produces a positive cable length change (i.e., cable is played out from the spool), and a negative motor rotation winds cable onto the spool.

After attaching the cables to the spools, the other end should be routed through the ~.9mm hole in the motor mount bracket.

## Effector

The end effector of this robot is a rectangular raft carrying several Hawkeye Technologies [IR-50](http://www.hawkeyetechnologies.com/source-selection/pulsable/) emitters. The robot drives the centroid of the effector to a specified position, and the control algorithm performs a specific sequence of flashes using a number of the emitters to enhance the detectability of the signal in the TIME receiver output data.

The effector is attached to the cables by simply wrapping ends of the fishing line around the screws in each corner of the raft and screwing them down.

## Frame

The 3D printed CFRP stepper motor mounts are attached to the beam mapper frame by 5/16-18 x 2" or 2.25" bolts with nyloc "jam" nuts.

A 3D printed CFRP "homing bar" with a corner reference feature sticks out into the mapping region to provide a repeatable location for placing the corner of the effector raft. This part is attached to the beam mapper frame with one 5/16-18 x 2" or 2.25" bolt with nyloc "jam" nut. Ensure the arm is pressed flat against the inside of the frame, no matter where it is attached.

Four 3D printed CFRP 3" x 2.5" registration tabs are provided to enhance the clamping surface the frame can use along the perimeter of a given mirror. They should be installed with 5/16-18 x 2" or 2.25" bolts with nyloc "jam" nuts, installed on the interior of the frame, and oriented such that they extend "down" from the frame, opposite the motor mount brackets. They can be installed in any location along the frame, provided they avoid contact with the mirror's laser tracker nest tabs when the frame is mounted to the mirror.

Two aluminum registration tabs are screwed into the end of each frame piece opposite the black plastic end caps, using a 5/16-18 x 1/4" screw. They are long enough to reach an edge of the mirror regardless of if the mirror's corners have been machined off. These tabs register the frame to a third edge of the mirror, so **it is important that they not be bent**.

When all of these pieces are attached to the frame, it is ready to install onto a mirror for mapping.

# Documentation
## `pycallgraph`
To re-generate the call graph image, from the `src` directory, run
```
pycallgraph -i "alg*" -i "const*" -i "exec*" -i "hardw*" -i "hot*" -i "hw*" -i "tele*" graphviz --output-file=../doc/img/pycallgraph.png -- ./hotspot.py ../data/input/geometry/frame.csv ../data/input/profiles/box_frame.csv
```
You must have `graphviz` installed (using your operating system's package manager).

# Test Fixture Setup

For testing the software and hardware together, we set up the raspberry pi and the steppers on an optics bench in Steward Observatory Lab 168. This allows us to affix the steppers to something a roughly known distance apart.

## Stepper Fixture

Steppers are attached to the optics bench for testing via 3D-printed brackets. 1/4-20 socket head cap screws affix the bracket to the bench, and M3 screws affix the steppers to the brackets.
<img src="img/spool_side_view.jpg" alt="drawing" width="200"/> <img src="img/spool_bench_mounted.jpg" alt="drawing" width="200"/>

## Fishing line routing

On the optics bench, the fishing line was routed from the motor spools to the raft via 3D printed posts, forming 4 corners of a rectangle to emulate the operational configuration. These posts were 3D printed 1/4-20 screws in PETG plastic, with ~.9mm (as designed, not as printed) holes in the top to allow routing the fishing line through.

## Test raft

For testing purposes, the raft was another 3D printed part, a rectangular plastic coupon with four holes to accept M3 screws for tying down the ends of the fishing line a known distance apart. This was done in lieu of having a raft of Hawkeye sources ready.

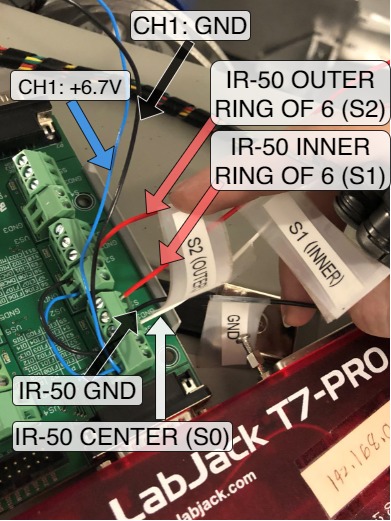
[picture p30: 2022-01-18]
docs/html/docs/img/labjack_wiring.jpeg

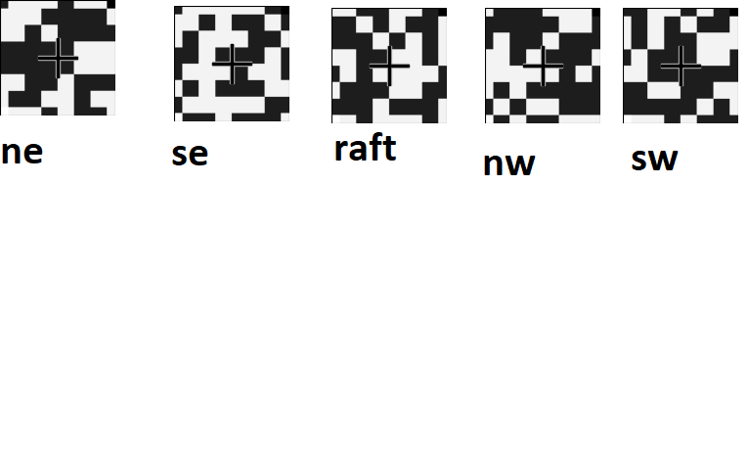
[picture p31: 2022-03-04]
verification/targets/target_printout.png

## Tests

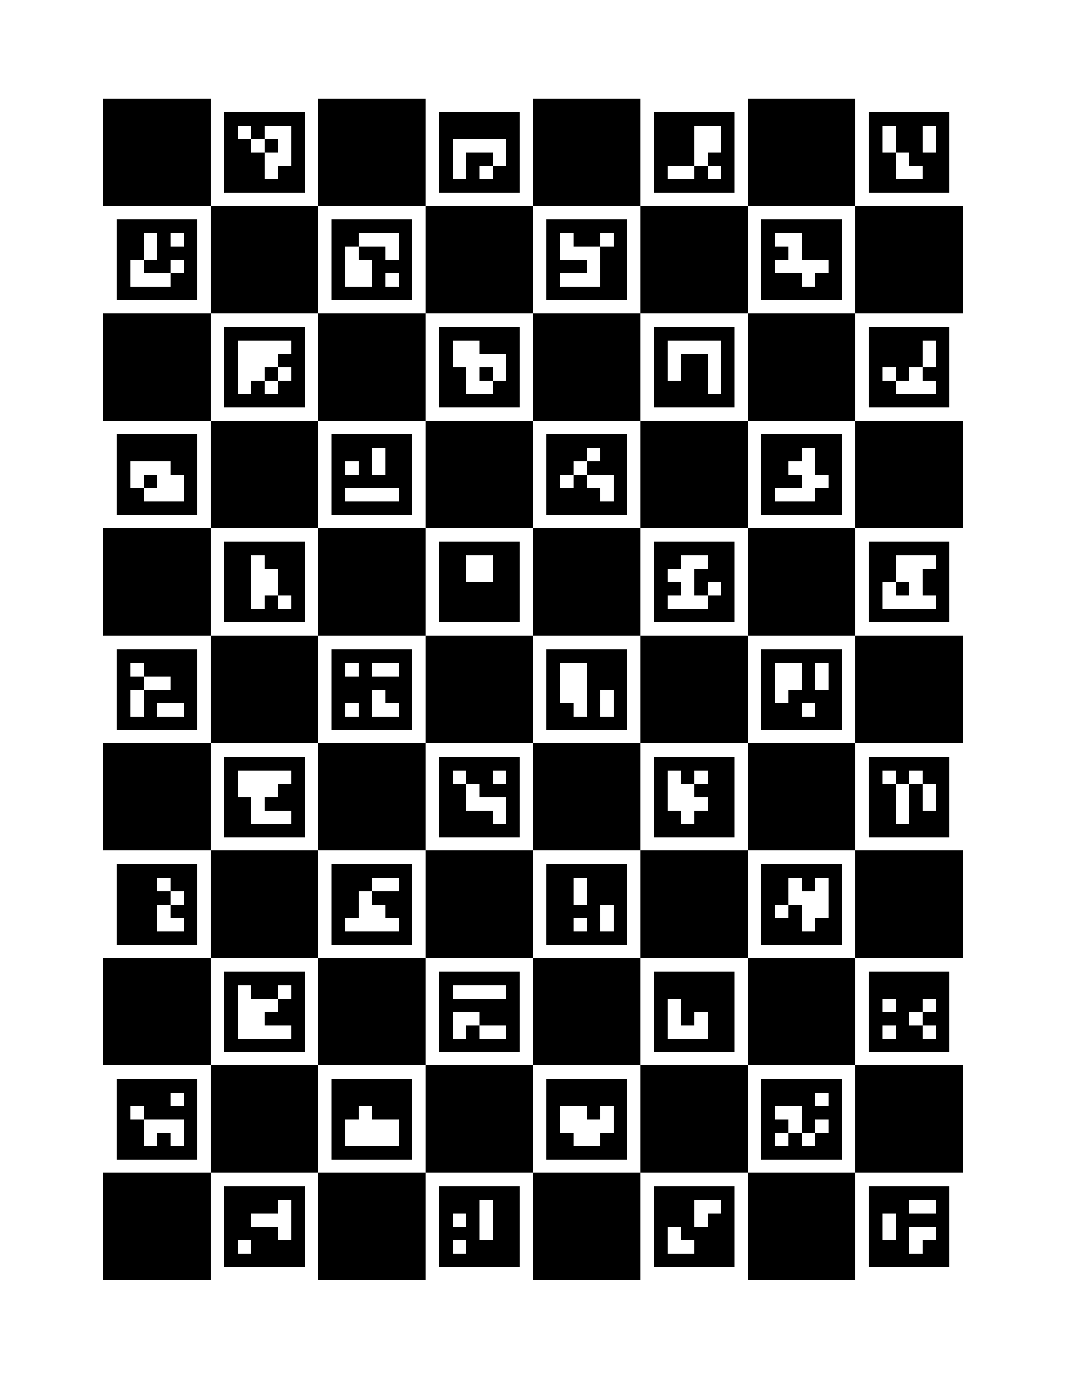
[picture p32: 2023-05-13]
verification/8x11_square_0.02m_aruco_0.015m_charuco_dict_3.png

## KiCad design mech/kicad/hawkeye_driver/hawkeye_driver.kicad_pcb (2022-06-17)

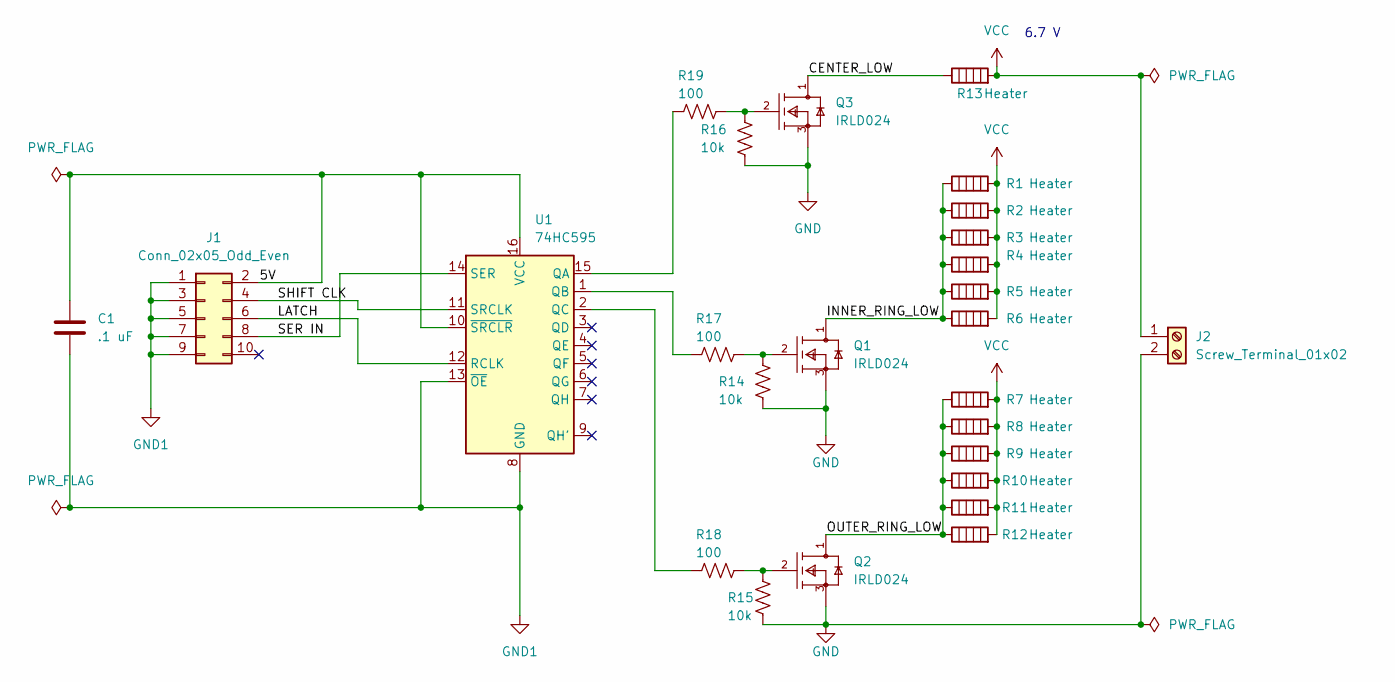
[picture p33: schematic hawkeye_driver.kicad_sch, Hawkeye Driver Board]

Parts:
C1: .1 uF; C_1206_3216Metric_Pad1.33x1.80mm_HandSolder
J1: Conn_02x05_Odd_Even; IDC-Header_2x05_P2.54mm_Vertical
J2: Screw_Terminal_01x02; TerminalBlock_Philmore_TB132_1x02_P5.00mm_Horizontal
Q1, Q2, Q3: IRLD024; Vishay-IRLD024-0; voltage 10V; mouser part number 844-IRLD024; digikey description MOSFET N-CH 60V 2.5A 4-DIP
R1, R2, R3, R4, R5, R6, R7, R8, R9, R10, R11, R12, R13: Heater; TO-5-3_Window
R14, R15, R16: 10k; R_1206_3216Metric_Pad1.30x1.75mm_HandSolder
R17, R18, R19: 100; R_1206_3216Metric_Pad1.30x1.75mm_HandSolder
U1: 74HC595; SO-16_3.9x9.9mm_P1.27mm

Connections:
/5V: C1.1, J1.2, U1.10 (~SRCLR), U1.16 (VCC)
/CENTER_LOW: Q3.1 (D), R13.1
/INNER_RING_LOW: Q1.1 (D), R1.1, R2.1, R3.1, R4.1, R5.1, R6.1
/LATCH: J1.6, U1.12 (RCLK)
/OUTER_RING_LOW: Q2.1 (D), R7.1, R8.1, R9.1, R10.1, R11.1, R12.1
/SER IN: J1.8, U1.14 (SER)
/SHIFT CLK: J1.4, U1.11 (SRCLK)
GND: J2.2, Q1.3 (S), Q2.3 (S), Q3.3 (S), R14.2, R15.2, R16.2
GND1: C1.2, J1.1, J1.3, J1.5, J1.7, J1.9, U1.8 (GND), U1.13 (~OE)
unnamed: Q1.2 (G), R14.1, R17.2
unnamed: Q2.2 (G), R15.1, R18.2
unnamed: Q3.2 (G), R16.1, R19.2
unnamed: R17.1, U1.1 (QB)
unnamed: R18.1, U1.2 (QC)
unnamed: R19.1, U1.15 (QA)
VCC: J2.1, R1.2, R2.2, R3.2, R4.2, R5.2, R6.2, R7.2, R8.2, R9.2, R10.2, R11.2, R12.2, R13.2

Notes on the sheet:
6.7 V

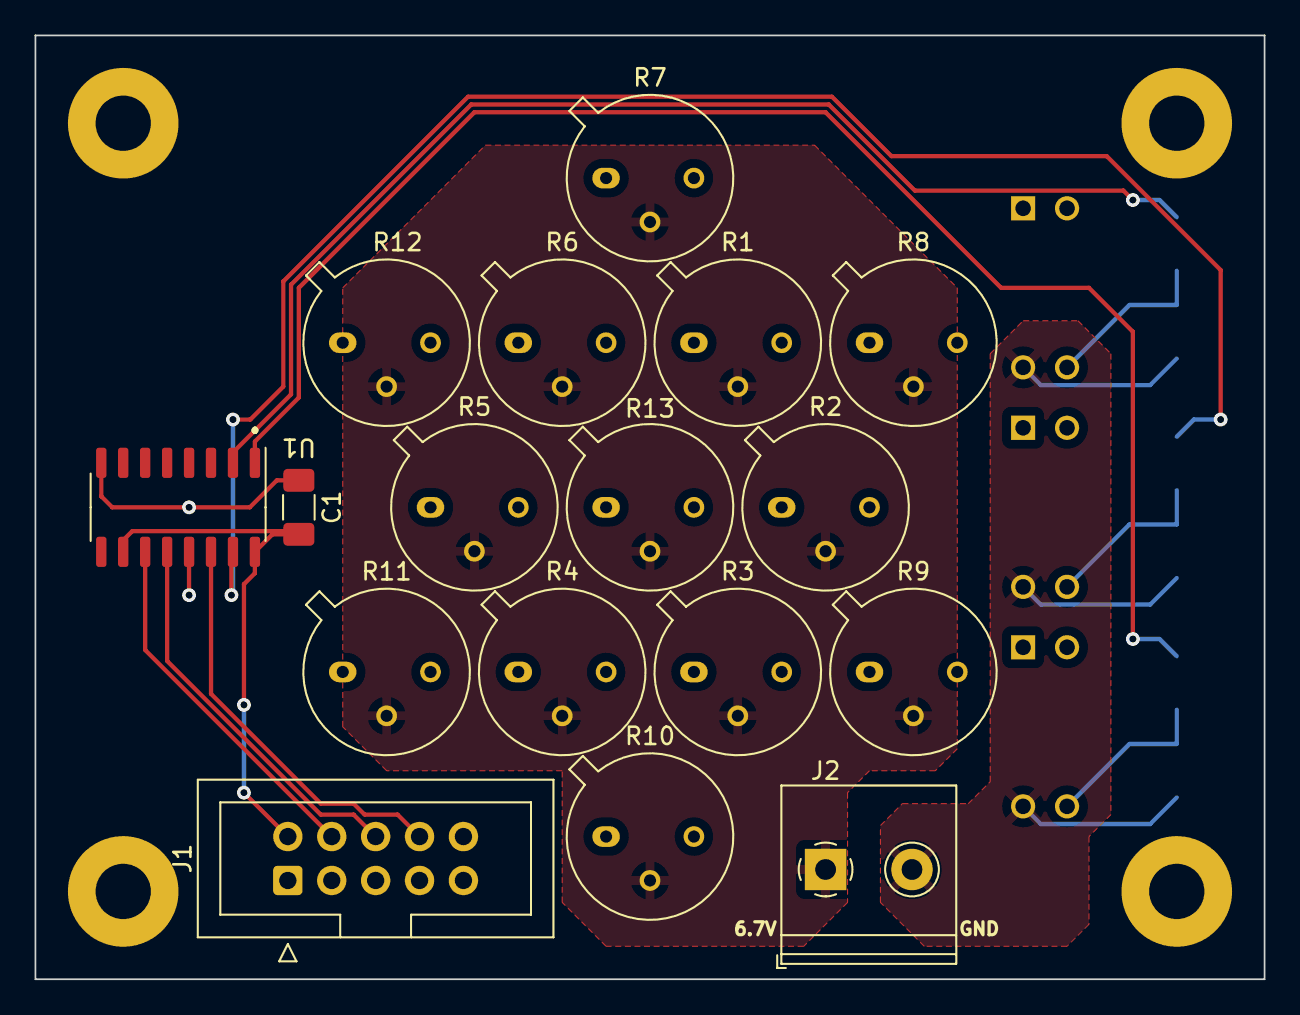
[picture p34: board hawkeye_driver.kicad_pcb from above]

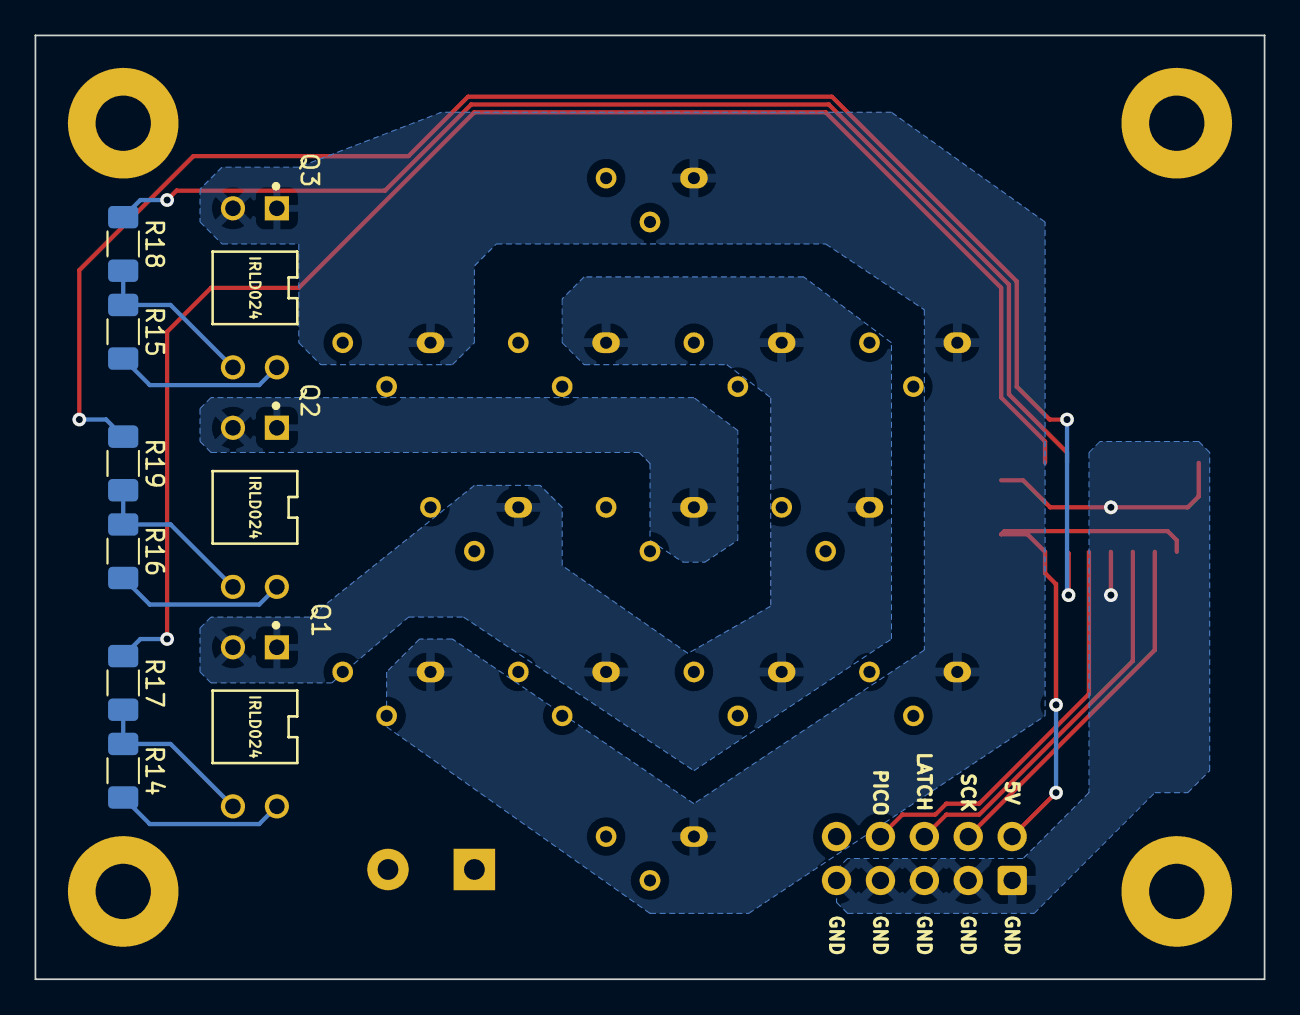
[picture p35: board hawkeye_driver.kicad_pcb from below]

Board: 2 copper layers, 71.1 x 54.6 mm, 26 parts (9 on the bottom side), 16 nets.

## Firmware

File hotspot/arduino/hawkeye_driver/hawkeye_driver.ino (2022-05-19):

//**************************************************************//
//  Name    : shiftOutCode, Hello World
//  Author  : Carlyn Maw,Tom Igoe, David A. Mellis
//  Date    : 25 Oct, 2006
//  Modified: 23 Mar 2010
//  Version : 2.0
//  Notes   : Code for using a 74HC595 Shift Register           //
//          : to count from 0 to 255
//****************************************************************

//Pin connected to ST_CP of 74HC595
int latchPin = 4;
//Pin connected to SH_CP of 74HC595
int clockPin = 3;
////Pin connected to DS of 74HC595
int dataPin = 2;

void setup() {
  //set pins to output so you can control the shift register
  pinMode(latchPin, OUTPUT);
  pinMode(clockPin, OUTPUT);
  pinMode(dataPin, OUTPUT);
}

void loop() {
  // take the latchPin low so
  // the LEDs don't change while you're sending in bits:
  digitalWrite(latchPin, LOW);
  // shift out the bits:
  shiftOut(dataPin, clockPin, MSBFIRST, 0);
  //take the latch pin high so the LEDs will light up:
  digitalWrite(latchPin, HIGH);
  // pause before next value:
  delay(500);
  
  digitalWrite(latchPin, LOW);
  shiftOut(dataPin, clockPin, MSBFIRST, 7);
  digitalWrite(latchPin, HIGH);
  delay(500);
}

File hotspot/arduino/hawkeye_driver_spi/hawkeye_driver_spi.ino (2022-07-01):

// This program writes a byte from serial input to an SPI output.
// The SPI peripheral is a shift register, 74HC595.
#include <Adafruit_DotStar.h>
#include <SPI.h>


// payload from serial
char data;
// ST_CP of 74HC595
int latchPin = 2;
SPISettings settings;
// activity indicators
int ledPin = 13;
Adafruit_DotStar onBoard = Adafruit_DotStar(1, INTERNAL_DS_DATA, INTERNAL_DS_CLK, DOTSTAR_BGR);


void setup()
{
    Serial.begin(115200);

    SPI.begin();
    settings = SPISettings(1500000, MSBFIRST, SPI_MODE0);
    SPI.beginTransaction(settings);

    pinMode(latchPin, OUTPUT);
    pinMode(ledPin, OUTPUT);
    onBoard.begin();
    onBoard.show();
}


void writeByteSPI(long data)
{
    SPI.beginTransaction(settings);
    digitalWrite(latchPin, LOW);
    SPI.transfer(data);
    digitalWrite(latchPin, HIGH);
    SPI.endTransaction();
}


void loop()
{
    while (Serial.available() > 0)
    {
        // No timeout; intentionally hangs until next byte comes in.
        data = Serial.parseInt();
        writeByteSPI(data);
        if (data > 0)
        {
            digitalWrite(ledPin, HIGH);
            // interpret 3 bits of the 8-bit char as channels in RGB.
            onBoard.setPixelColor(0, \
                (data & 0b001) * 255,\
                (data & 0b010) * 255,\
                (data & 0b100) * 255\
            );
            onBoard.setBrightness(75);
            onBoard.show();
        }
        else
        {
          digitalWrite(ledPin, LOW);
          onBoard.setBrightness(10);
          onBoard.show();
        }
    }
}

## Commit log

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2021-10-16 nema17 flange to optics bench bolt pattern
    [nema_17_to_optics_bench.stl]
2021-10-16 spool v0
    [spool.stl]
2021-10-18 spool v2
    [spool.stl]
2021-10-18 add modeled threads (m3)
    [spool.stl]
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2021-10-21 move stepper chirp data products
    [freq_vs_omega.csv]
2021-10-25 Improve chirp test and record results
    [cmd_vs_est.csv]
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2021-10-27 work on executive
    [test.csv]
2021-10-27 Wrote barebones executive
    [test.csv]
2021-10-27 add second hat, remove relevant TODOs
    [test.csv]
2021-10-27 switched motor runner to subprocess, all tests passing
    [test.csv]
2021-10-28 test input files
    [box.csv, test.csv, x.csv]
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2021-10-28 implement homing calibration and home modes.
    [box.csv, test_surface.csv, x.csv]
2021-10-30 Data logger and visualization written
    [box.csv]
2021-10-30 remove jog mode, add a raster scan profile
    [raster_10cm.csv]
2021-10-30 add 5cm radius circule profile
    [circle_r5cm.csv]
2021-11-01 lab benchtop setup
    [box.csv]
2021-11-01 dont forget lab bench geom file
    [lab_bench.csv]
2021-11-01 pause to update TM and plots after each move.
    [raster_2cm.csv]
2021-11-09 prototype single threaded motoring
    [box.csv, raster_2cm.csv]
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2021-11-10 add bresenahm's stepping function
    [lab_bench.csv]
2021-11-10 remove async motor commanding and everything related to speed control
    [box.csv, circle_r3cm.csv, circle_r5cm.csv, raster.csv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]
2021-11-10 stepping mode to double, updates to input files
    [circle.csv, x.csv]
2021-11-11 add stls for test bench setup, and version motor spool stl
    [cable_post_v2.stl, raft_proto_v2.stl, spool.stl]
2021-11-23 updates to mech stls
    [cable_post_v2.stl, motor_mount.stl]
2021-11-23 add extra holes to motor mount
    [motor_mount.stl]
2021-11-24 first cut at beam mapper config files
    [box_frame.csv, frame.csv]
2021-11-27 logging and bugfixes
    [box_frame.csv, circle.csv]
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2021-11-28 rename doc folder to docs, add pdoc html documentation, .md updates
    [cmd_vs_est.csv, freq_vs_omega.csv]
2021-11-29 update frame geom with new measurements. home should be .15, .225.
    [frame.csv]
2021-11-29 debugging updates
    [box_frame.csv, point.csv]
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2021-12-03 first cut lj integration, with necessary input file changes
    [box.csv, box_frame.csv, circle.csv, point.csv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]
2021-12-04 LabJack fully integrated and benchtop tested
    [point.csv]
2021-12-04 docs and frame meas update
    [frame.csv]
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2021-12-23 experimental homing algorithm
    [24in_breadboard.csv, frame.csv, lab_bench.csv]
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2022-01-03 edit profiles for 24in box debugging
    [box_frame.csv, circle_frame.csv, point.csv, raster.csv]
2022-01-04 input file changes
    [24in_breadboard.csv, box_frame.csv, point.csv]
2022-01-04 more debugging, verified hawkeye sources work at least
    [point.csv]
2022-01-05 Remove hacks from executive, not actually necessary
    [point.csv]
2022-01-05 Accounting of net steps taken, help w/ rounding error
    [point.csv]
2022-01-06 Unused code cleanup
    [point.csv]
2022-01-07 Create profiles for TIME optics
    [F1.csv, K1.csv, K2.csv, K3.csv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]
2022-01-07 Create geometry input files for TIME optics
    [F1.csv, K1.csv, K2.csv, K3.csv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]
2022-01-07 remove unused profiles
    [box.csv, raster.csv, x.csv]
2022-01-07 rename profiles to reflect what's inside
    [F1_raster.csv, K1_raster.csv, K2_raster.csv, K3_raster.csv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]
2022-01-07 fixed incorrect measurements of x-offsets
    [24in_breadboard.csv]
2022-01-07 this version actually kind of works!
    [point.csv]
2022-01-09 Fix create_geometry typo
    [F1.csv, K1.csv, K2.csv, K3.csv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]
2022-01-12 coarse raster scans
    [F1_raster_coarse.csv, K1_raster_coarse.csv, K2_raster_coarse.csv, K3_raster_coarse.csv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]
2022-01-12 update scan pattern of coarse files for photogrammetry
    [F1_raster_coarse.csv, K1_raster_coarse.csv, K2_raster_coarse.csv, K3_raster_coarse.csv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]
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2022-01-14 new profiles for photo-g starting NW instead of SE
    [F1_raster_coarse_NW.csv, K1_raster_coarse_NW.csv, K2_raster_coarse_NW.csv, K3_raster_coarse_NW.csv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]
2022-01-14 upload photos and results, add a new scan for comore complete coverage of 24 in breadboard surface
    [24in_breadboard_raster_large_coverage.csv]
2022-01-15 0.001 inch adjust to K2
    [K2.csv]
2022-01-16 add larger footprint coarse scans
    [24in_breadboard_raster_coarse_.2x.2.csv, F1_raster_coarse_.2x.2.csv, K1_raster_coarse_.2x.2.csv, K2_raster_coarse_.2x.2.csv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]
2022-01-16 more dense pattern
    [24in_breadboard_raster_7x7_.15x.15.csv, F1_raster_7x7_.15x.15.csv, K1_raster_7x7_.15x.15.csv, K2_raster_7x7_.15x.15.csv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]
2022-01-16 add 9x9 profile
    [24in_breadboard_raster.csv, 24in_breadboard_raster_9x9_.2x.2.csv, F1_raster_9x9_.2x.2.csv, K1_raster_9x9_.2x.2.csv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]
2022-01-16 create profiles with an additional flasher address for 5V output to MCE clock card
    [24in_breadboard_raster.csv, 24in_breadboard_raster_9x9_.2x.2.csv, 24in_breadboard_raster_coarse_NW.csv, 24in_breadboard_raster_large_coverage.csv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]
2022-01-16 change MCE clk out address
    [24in_breadboard_raster.csv, 24in_breadboard_raster_9x9_.2x.2.csv, 24in_breadboard_raster_coarse_NW.csv, 24in_breadboard_raster_large_coverage.csv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]
2022-01-17 make K1 profiles use only 1 hawkeye
    [K1_raster.csv, K1_raster_9x9_.2x.2.csv, K1_raster_coarse_NW.csv]
2022-01-17 add 7 hawkeye K1 scan
    [K1_raster.csv, K1_raster_9x9_.2x.2.csv, K1_raster_coarse_NW.csv]
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2022-01-21 fix 24in input file
    [24in_breadboard.csv]
2022-01-24 add cable spool charatcerization
    [16x_microsteps_vs_distance_m.csv]
2022-01-26 second try at characterizing angle vs. distance
    [16x_microsteps_vs_distance_m_v2.csv]
2022-01-27 update geometry for aymmetrical motor mounts and fix x-coord bug
    [F1.csv, K1.csv, K2.csv, K3.csv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]
2022-01-27 bugfix 24in input file
    [24in_breadboard.csv]
2022-01-28 experimentally determining k and r
    [point.csv]
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2022-01-29 run update on geo files
    [24in_breadboard.csv, F1.csv, K1.csv, K2.csv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]
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2022-05-17 init hawkeye driver kicad commit
    [cable_post_v2.stl, hawkeye_raft.stl, home_bar.stl, motor_mount.stl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]
2022-05-17 hawkeye driver kicad
    [hawkeye_driver-B_Cu.gbr, hawkeye_driver-B_Mask.gbr, hawkeye_driver-B_Paste.gbr, hawkeye_driver-B_Silkscreen.gbr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]
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2022-05-19 work on ground planes
    [hawkeye_driver.kicad_pcb, hawkeye_driver.kicad_sch]
2022-05-19 finish ground plane rework
    [hawkeye_driver.kicad_pcb, hawkeye_driver.kicad_sch]
2022-05-20 minor pcb silkscreen edits
    [hawkeye_driver.kicad_pcb]
2022-05-20 final commit before fab
    [hawkeye_driver.kicad_pcb, hawkeye_driver.kicad_sch]
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2022-06-05 update mosfet silkscreen and soldermask for errors
    [hawkeye_driver.kicad_pcb]
2022-06-05 doc updates
    [16x_microsteps_vs_distance_m.csv, 16x_microsteps_vs_distance_m_v2.csv]
2022-06-07 fudge factor in gometry filegit add data/input/geometry/24in_breadboard.csv !
    [24in_breadboard.csv]
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2022-06-15 update geometry files with new raft eyelet dimensions
    [24in_breadboard.csv, F1.csv, K1.csv, K2.csv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]
2022-06-17 docs updates, pcb updates, photogrammetry updates
    [box_frame.csv, hawkeye_driver.kicad_pcb]
2022-06-17 possible targetless raft tracking
    [hawkeye_driver-B_Cu.gbr, hawkeye_driver-B_Mask.gbr, hawkeye_driver-B_Silkscreen.gbr, hawkeye_driver-Edge_Cuts.gbr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]
2022-07-01 switch from labjack hawkeye driver to microcontroller driver
    [24in_breadboard_raster.csv, 24in_breadboard_raster_7x7_.15x.15.csv, 24in_breadboard_raster_9x9_.2x.2.csv, 24in_breadboard_raster_coarse_.2x.2.csv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]
2022-07-12 general code cleanup
    [24in_breadboard.csv, F1.csv, K1.csv, K2.csv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]
2022-07-18 update geometry after modifying motor mounts to accommodate encoder stickout
    [24in_breadboard.csv, F1.csv, K1.csv, K2.csv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]
2022-07-21 update photogrammetry
    [24in_breadboard_raster_skipline_18x18_.2x.2.csv, F1_raster_skipline_18x18_.2x.2.csv, K1_raster_skipline_18x18_.2x.2.csv, K2_raster_skipline_18x18_.2x.2.csv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]
2022-08-03 Lasts doc updates, geometry updates, profile update
    [24in_breadboard.csv, 24in_breadboard_raster.csv, 24in_breadboard_raster_7x7_.15x.15.csv, 24in_breadboard_raster_skipline_4x4_0.20x0.20.csv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]
2022-08-03 profile updates
    [24in_breadboard_raster_skipline_10x10_0.30x0.30.csv, F1_raster_skipline_10x10_0.30x0.30.csv, K1_raster_skipline_10x10_0.30x0.30.csv, K2_raster_skipline_10x10_0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]
2022-08-08 Major updates and cleanup to profiles dir
    [24in_breadboard_raster.csv, 24in_breadboard_raster_20x20_0.20mx0.20m.csv, 24in_breadboard_raster_9x9_.2x.2.csv, 24in_breadboard_raster_coarse_.2x.2.csv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]
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2023-05-26 Performance fixes and bug improvements
    [25in_breadboard.csv]
2023-06-09 Bring STLs up to date with reality
    [drum.stl, hawkeye_raft.stl, motor_mount_thin.stl, motor_mount_thin_mirror.stl]
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2024-12-16 Profile cleanup: delete those I don't anticipate to use for TIME 2024/2025
    [24in_breadboard_raster_skipline_10x10_0.30mx0.30m.csv, 24in_breadboard_raster_skipline_18x18_0.30mx0.30m.csv, 24in_breadboard_raster_skipline_4x4_0.30mx0.30m.c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]
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
